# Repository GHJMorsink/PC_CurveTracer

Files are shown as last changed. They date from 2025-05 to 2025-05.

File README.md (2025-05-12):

# PC_CurveTracer

*Curve tracing for bjt transistors, FETs, diodes and more through ATMega micro and PC*

## Introduction

This project builds an I-V Curve Tracer connected to a computer using USB. A curve tracer is a type of instrument used to 
measure the current through a device with varying voltages across it. It is a specialized piece of electronic test equipment 
to analyze the characteristics of discrete electronic components, such as diodes, and transistors. The device contains 
voltage and current sources that can be used to stimulate the device under test (DUT). The curve tracer applies a continuously 
varying voltage to two terminals of the device under test and measure the amount of current that the device permits to flow 
at each voltage. This so-called I-V (current versus voltage) data is directly displayed on an oscilloscope screen in X-Y mode.
Examples of full featured Curve tracers which can go to more than 100 Volt and currents into several amps are the Textronix 576, 577, 
and the Leader LTC-905. Simpler (and cheaper) solutions are based on a simple transformer with a few resistors like 
in [Changpuak's curvetracer](https://www.changpuak.ch/electronics/Curve_Tracer_advanced.php). All of these need an oscilloscope 
as the display device.
This project builds one which does not use an oscilloscope, but shows the data, and the controls on a computer. The interface 
to the computer is through USB, and the power is also taken from the USB connection. This means the device can only handle 
signal-sized discrete components up to 5 Volt and a maximum of about 10 mAmpere.

## Hardware

The hardware used is based on a simple microcontroller (good old Atmel ATMega8) which generates the varying voltages with two PWM-DAC based outputs. 
The measurements are done with the internal ADC. For switching between NPN and PNP transistors (or N-mosfets and P-mosfets) one 
of the digital outputs is used.
The USB connection is based on the V-USB package of OBDev [V-USB](https://github.com/obdev/v-usb).
The power section for the DUT contains an opamp for buffering the DAC output, so it can sink and source currents. The resistor 
measures the current and creates at the same time a current limiting function. The second opamp is arranged as a current to 
voltage convertor with some gain so that about 10 mA gives a full scale for the ADC. Note that the ground reference for the 
floating current convertor is switched to accommodate for positive and negative currents. Also be aware the opamp’s inputs 
and outputs must reach rail to rail voltages. The control connection for the DUT (the base, or the gate) has fairly simple set-up 
from the second PWM-DAC with one RC-filter and a high value resistor; FETs get a voltage, bipolar transistors get a small current.

## Firmware

To be able to connect to the device without needing a software driver, the system will work as a HID device. Communication will 
be on the features report channel. The device and the used protocol has the capacity for 16 different modes with each 8 functions. 
At the moment only the mode for measuring a trace and resetting (for firmware updates) are implemented. The functions are 
initializing, reading measurements, and reading and setting calibration data. More modes and funtions can be created in the 
future; there is still enough room on an ATMega8. One can think of an automated hFE measurement mode and likewise modes for FETs.
Creating one trace is done by the initializing command containing the info for the used bias voltage (and this determines 
directly the bias current in cases of bipolar transistors), the number of measurement points, and the polarity to be used. 
After the initialization the requested number of measurements can be retrieved. There are also commands for setting and reading 
calibration values, which are needed for correction of the current to voltage conversion. The calibration is used at PC 
software level, and stored on the device because it is 'attached' to the components of that device.

The firmware contains a hid-based usb bootloader. This helps in a simple system where updates of the firmware can be transported 
conveniently to the device. The software supports this mechanism (it was used heavily during development).

## Software

The controlling GUI is built using a Python script. The graphics are made using the PyQT and pyqtgraph packages. The connection 
with the device is through USB using the pywinusb package. Starting the GUI through main.py gives the following window:
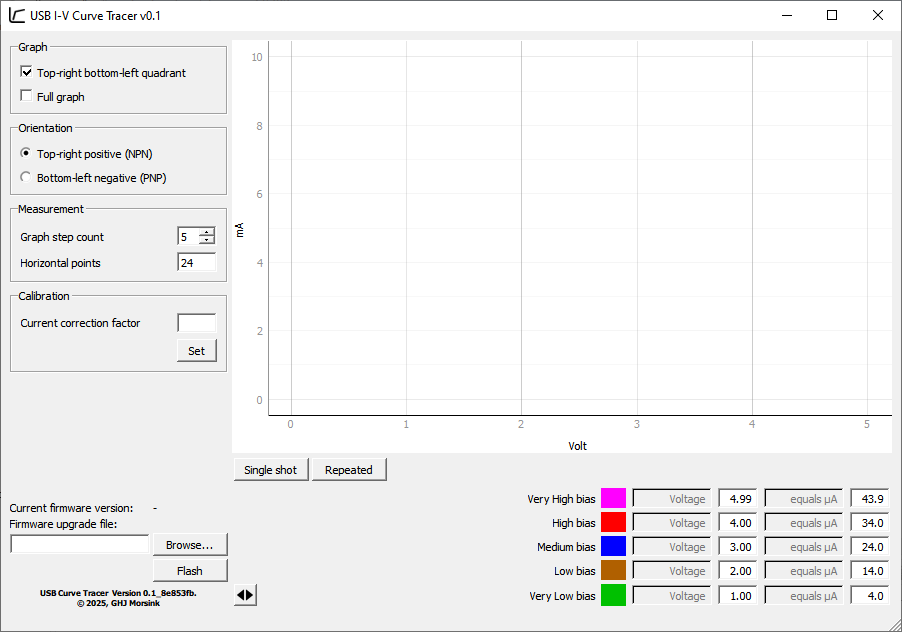
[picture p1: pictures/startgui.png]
startup image


It defaults to top-right quadrant for 5 traces, good for a normal npn transistor.

Within the application it is possible to update the firmware, so new features can be introduced. There is also a bootload.py 
script which gives the possibility to update the firmware or give it the initial firmware using the console.

## Results and calibration

Connecting the hardware to the computer, and starting the software conveniently through the CurveTracer.bat file gives the 
opportunity to calibrate it. This calibration is necessary only once. Put a 1kOhm resistor (1%) in the hardware between the collector 
and emitter pins, and do a 'single shot' measurement. You should see a straight line through points 0mA/0V,  1mA/1V,  2mA/2V, and 3mA/3V. 
If the line isn't correct, you can adjust it by changing the 'Current correction voltage', 'Set' it, and do a new measurement.
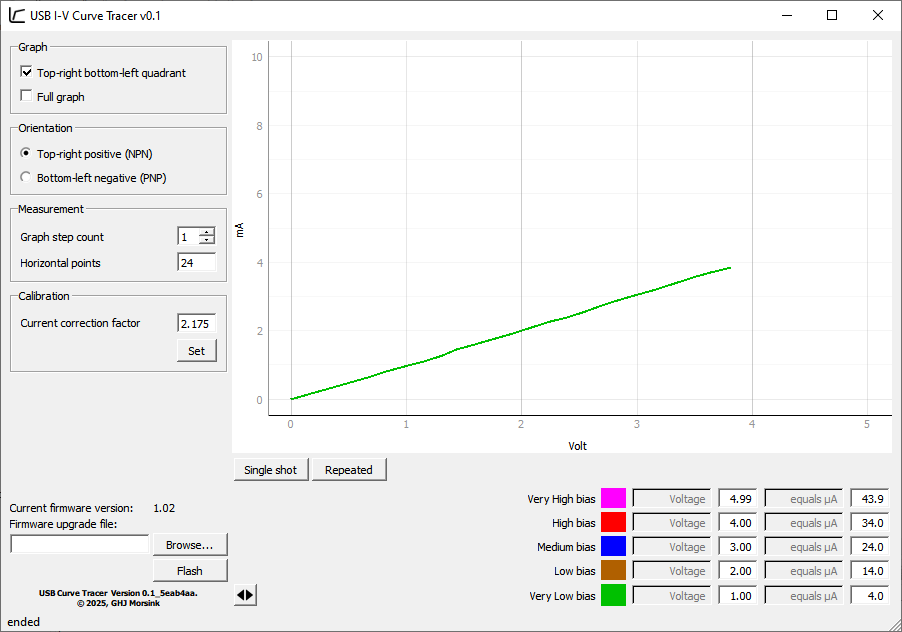
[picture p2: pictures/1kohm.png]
1kOhm image


A view of some other measurements are in the next pictures. A LED, a pnp transistor (BC213) and a npn transistor (2SC945). The last 
one in full graph mode: you get a single trace in the opposite quadrant, without any base/gate stimulation.
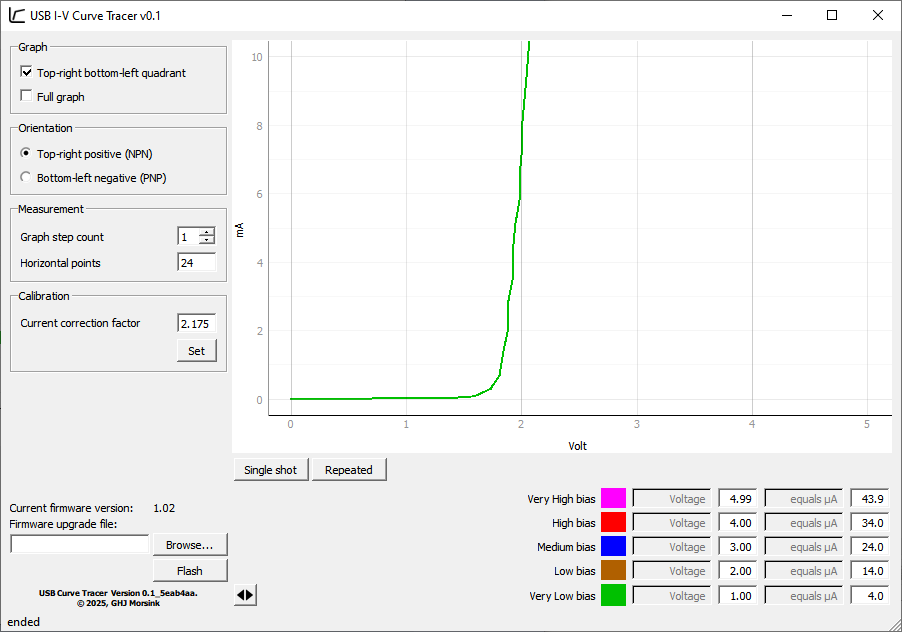
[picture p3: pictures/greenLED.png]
Green LED image

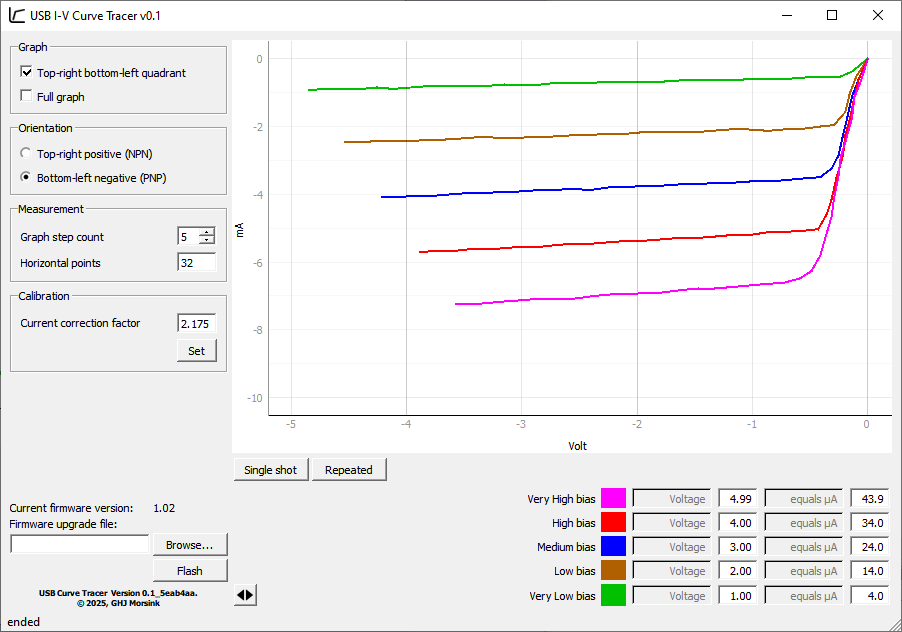
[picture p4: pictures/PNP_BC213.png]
BC213 PNP image

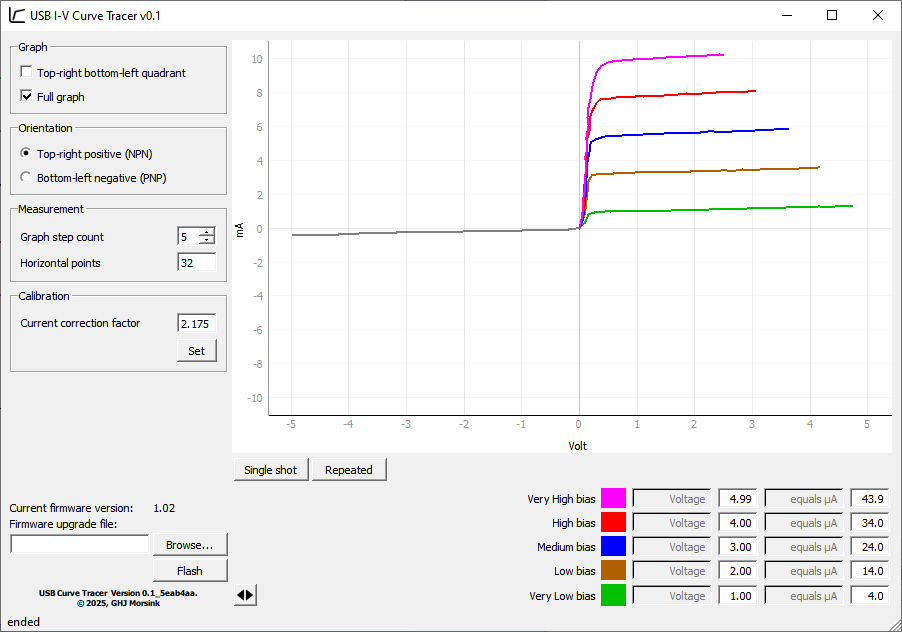
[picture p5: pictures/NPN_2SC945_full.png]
Full NPN 2SC945 image


Note: You can right-click on the graph for saving the picture and other goodies, supplied out of the box from the pyqtgraph package.

## Tooling and other notes

The hardware is developed with a somewhat older version of CadSoft's EAGLE pcb design software, now part of Autodesk Fusion Software.
Version 7.5.0 was used. For reference the schematic and the pcb design are also given as pdf document.
The firmware is written using the Microchip Studio 7.0 environment. You can get it through the URL [https://www.microchip.com/en-us/tools-resources](https://www.microchip.com/en-us/tools-resources/develop/microchip-studio#Downloads); older Atmel versions will work as well. 
The firmware is with minor or no changes also usable on the ATMega88 and the bigger ATMega168 and ATMega328. The fuse settings 
for the microcontroller can be found in the document [Fuses.txt](./embedded/fuses.txt).
For convenience a hex file containing the image for the application and the bootloader is in the file ./embedded/full.hex.
The PC software is fully based o Python. Version 3.12 was used during development, any version in the 3-series should be fine. 
The requirements.txt contains the names of the needed packages to conveniently install them using 'pip'. For users who want to 
adapt/develop the software to their likings, it is advised to install QT Designer as well.

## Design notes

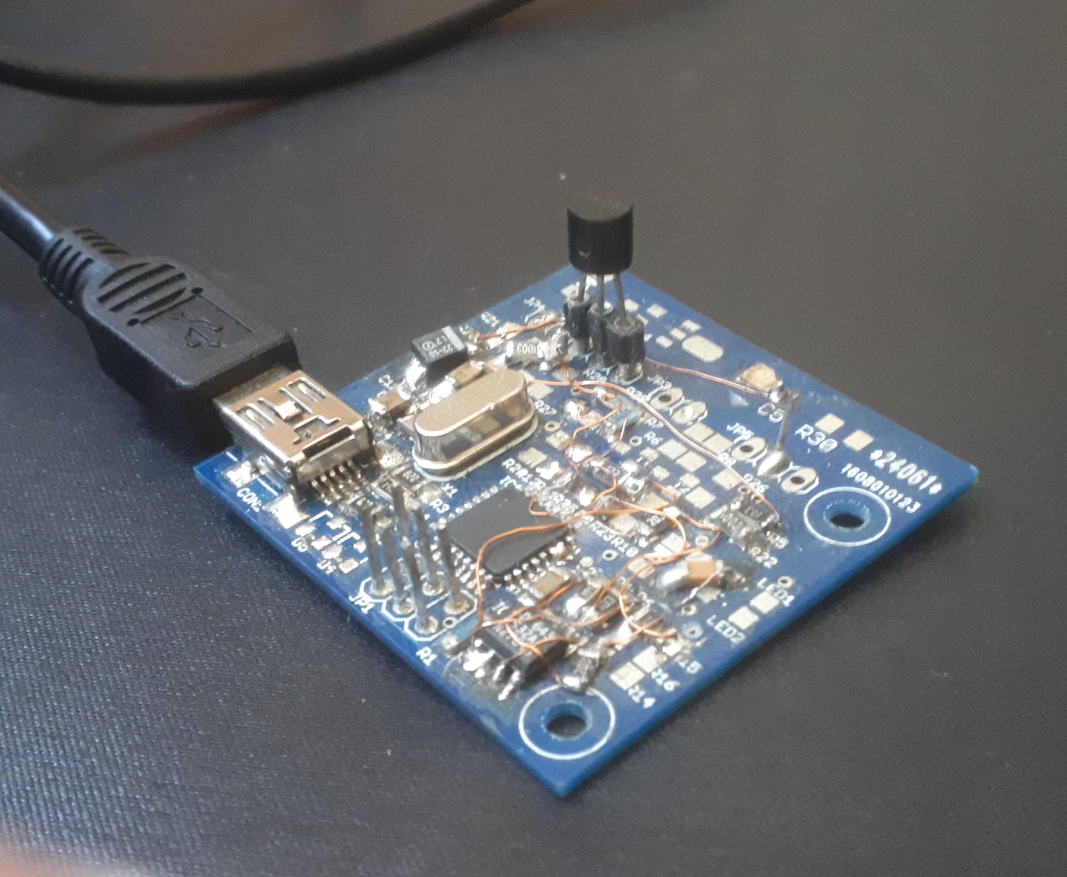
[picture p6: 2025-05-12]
pictures/prototype.jpg

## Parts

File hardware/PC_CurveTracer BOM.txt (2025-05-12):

Partlist exported from D:/projects/PC_CurveTracer/hardware/PC_CurveTracer.sch at 06/05/2025 17:49

Part Value     Device                       Package   Description                                MF MPN          NP OC_FARNELL OC_NEWARK VOLTAGE
C1   100n      C-EUC1206                    C1206     CAPACITOR, European symbol                                                                
C2   100n      C-EUC1206                    C1206     CAPACITOR, European symbol                                                                
C3   22p       C-EUC0603                    C0603     CAPACITOR, European symbol                                                                
C4   22p       C-EUC0603                    C0603     CAPACITOR, European symbol                                                                
C5   22n       C-EUC1206                    C1206     CAPACITOR, European symbol                                                                
C6   100n      C-EUC1206                    C1206     CAPACITOR, European symbol                                                                
C7   220p      C-EUC1206                    C1206     CAPACITOR, European symbol                                                                
C10  10uF      CPOL-EUSMCC                  SMC_C     POLARIZED CAPACITOR, European symbol                                               16V    
CON1 MINI-USB  MINI-USB_SHIELD5P4-32005-400 32005-400 MINI USB-B R/A W/O POST 5 pol.                                unknown    unknown          
D1   DUT       ZENER-DIODESOD80C            SOD80C    Z-Diode                                                                                   
D2   GREEN     LEDSML0805                   SML0805   LED                                                                                       
D3   BZX84C3V6 BZX84CSMD                    TO236     Z DIODE                                                    NP                             
D4   BZX84C3V6 BZX84CSMD                    TO236     Z DIODE                                                    NP                             
IC1  MEGA8-AI  MEGA8-AI                     TQFP32-08 MICROCONTROLLER                               ATMEGA8-16AU    9171371    73M8863          
IC2  TLC272B   LM358D                       SO08      OP AMP also LM158; LM258; LM2904                                                          
JP1  ISP       PINHD-2X3                    2X03      PIN HEADER                                                                                
JP2  SERIAL    PINHD-1X6                    1X06      PIN HEADER                                                                                
JP3  DEVICE    PINHD-1X5                    1X05      PIN HEADER                                                                                
L1   Ferrite   BLM15HG601SN1                0402      EMIFIL (R) Chip Ferrite Bead for GHz Noise                                                
R1   10K       R-EU_R1206                   R1206     RESISTOR, European symbol                                                                 
R2   82        R-EU_R1206                   R1206     RESISTOR, European symbol                                                                 
R3   82        R-EU_R1206                   R1206     RESISTOR, European symbol                                                                 
R4   1K8       R-EU_R1206                   R1206     RESISTOR, European symbol                                                                 
R5   470       R-EU_R1206                   R1206     RESISTOR, European symbol                                                                 
R6   220       R-EU_R1206                   R1206     RESISTOR, European symbol                                                                 
R7   10K       R-EU_R1206                   R1206     RESISTOR, European symbol                                                                 
R8   100K      R-EU_R1206                   R1206     RESISTOR, European symbol                                                                 
R9   47        R-EU_R1206                   R1206     RESISTOR, European symbol                                                                 
R10  100       R-EU_R1206                   R1206     RESISTOR, European symbol                                                                 
R11  20K       R-EU_R1206                   R1206     RESISTOR, European symbol                                                                 
R12  10K       R-EU_R1206                   R1206     RESISTOR, European symbol                                                                 
R13  20K       R-EU_R1206                   R1206     RESISTOR, European symbol                                                                 
R14  10K       R-EU_R1206                   R1206     RESISTOR, European symbol                                                                 
R15  10K       R-EU_R1206                   R1206     RESISTOR, European symbol                                                                 
T1   TUT       BC846                        SOT23     NPN TRANSISTOR                                                                            
T2   TUT       -PNP-SOT89-ECB               SOT89-ECB PNP Transistror                                                                           
X1   12MHz     CRYSTALHC49S                 HC49/S    CRYSTAL                                                       1667008    unknown

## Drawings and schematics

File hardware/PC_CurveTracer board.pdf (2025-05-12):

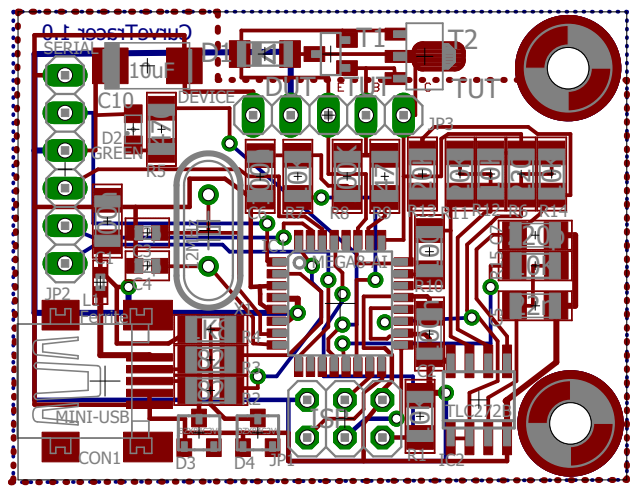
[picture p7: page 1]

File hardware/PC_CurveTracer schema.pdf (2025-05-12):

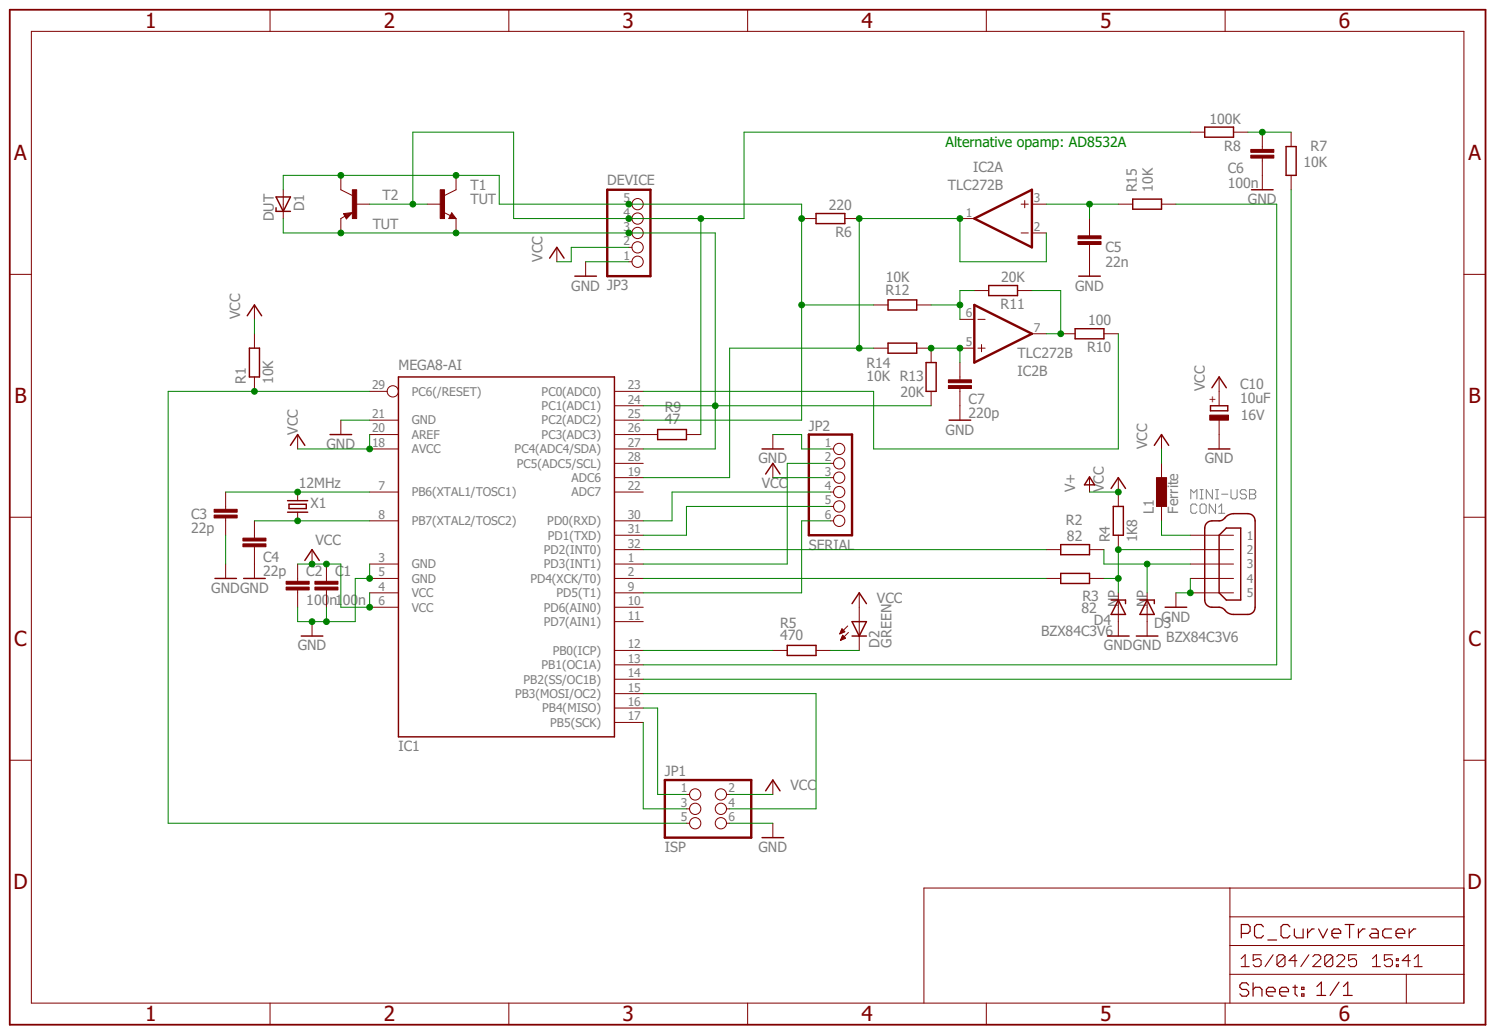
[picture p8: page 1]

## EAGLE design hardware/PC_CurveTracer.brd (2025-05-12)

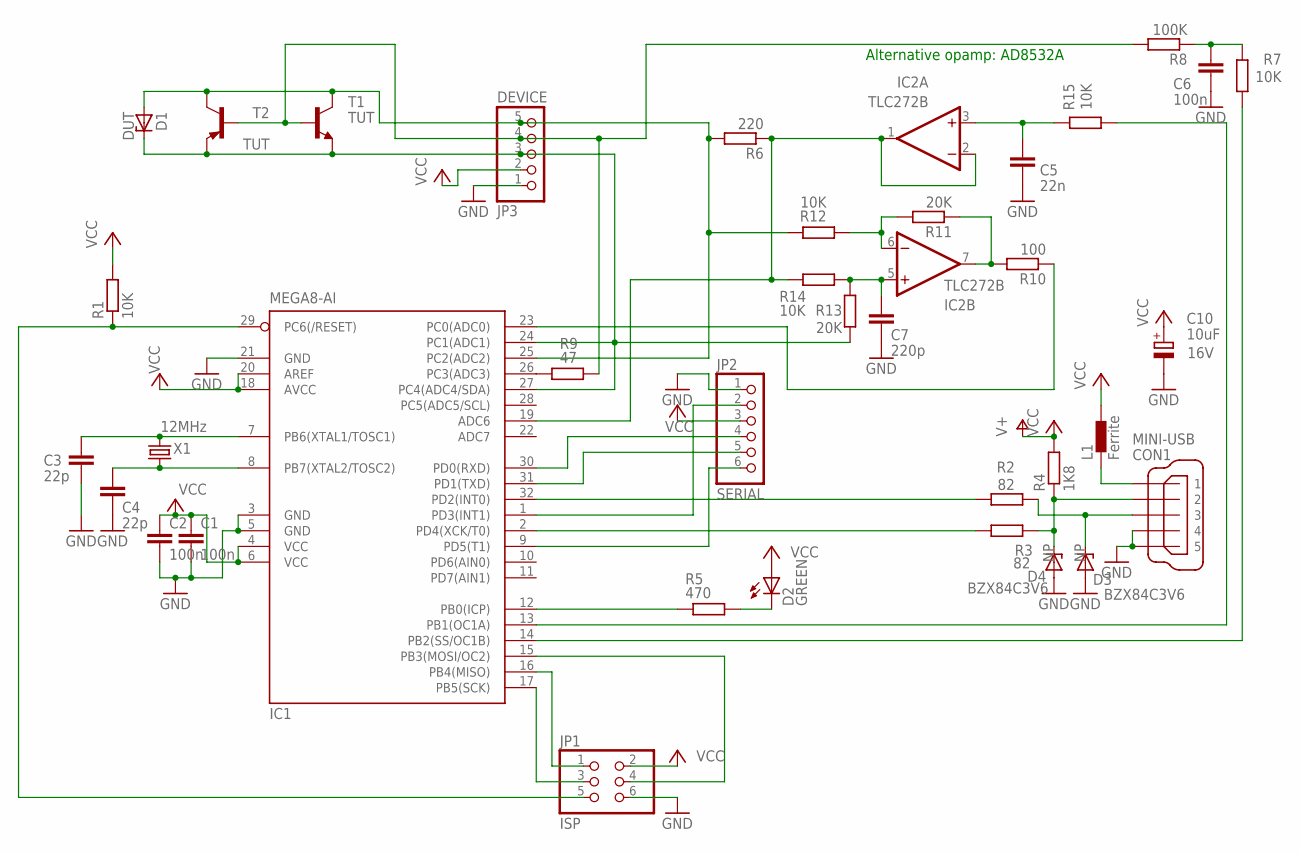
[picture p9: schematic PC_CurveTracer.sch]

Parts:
C1, C2, C6: 100n; C1206
C3, C4: 22p; C0603
C5: 22n; C1206
C7: 220p; C1206
C10: 10uF; SMC_C; VOLTAGE 16V
CON1: MINI-USB; 32005-400
D1: DUT; SOD80C
D2: GREEN; SML0805
D3, D4: BZX84C3V6; TO236
IC1: MEGA8-AI; TQFP32-08
IC2: TLC272B; SO08
JP1: ISP; 2X03
JP2: SERIAL; 1X06
JP3: DEVICE; 1X05
L1: Ferrite; 0402
R1, R7, R12, R14, R15: 10K; R1206
R2, R3: 82; R1206
R4: 1K8; R1206
R5: 470; R1206
R6: 220; R1206
R8: 100K; R1206
R9: 47; R1206
R10: 100; R1206
R11, R13: 20K; R1206
T1: TUT; SOT23
T2: TUT; SOT89-ECB
X1: 12MHz; HC49/S

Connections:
GND: C1.2, C2.2, C3.2, C4.2, C5.2, C6.2, C7.2, C10.-, CON1.4, CON1.5, D3.A, D4.A, IC1.3 (GND), IC1.5 (GND), IC1.21 (GND), IC2.4 (GND), JP1.6, JP2.1, JP3.1
unnamed: IC1.29 (PC6(/RESET)), JP1.5, R1.1
unnamed: D2.C, R5.1
unnamed: C3.1, IC1.7 (PB6(XTAL1/TOSC1)), X1.2
unnamed: C4.1, IC1.8 (PB7(XTAL2/TOSC2)), X1.1
unnamed: IC1.16 (PB4(MISO)), JP1.1
unnamed: CON1.1, L1.1
unnamed: IC1.15 (PB3(MOSI/OC2)), JP1.4
unnamed: IC1.12 (PB0(ICP)), R5.2
unnamed: IC1.32 (PD2(INT0)), R2.2
unnamed: IC1.1 (PD3(INT1)), JP2.2
unnamed: CON1.3, D3.C, R2.1
unnamed: IC1.30 (PD0(RXD)), JP2.4
unnamed: IC1.2 (PD4(XCK/T0)), R3.2
unnamed: CON1.2, D4.C, R3.1, R4.1
unnamed: IC1.13 (PB1(OC1A)), R15.1
unnamed: C6.1, R7.2, R8.1
unnamed: IC2.6 (-IN), R11.2, R12.1
unnamed: IC1.31 (PD1(TXD)), JP2.5
unnamed: D1.C, IC1.24 (PC1(ADC1)), IC1.27 (PC4(ADC4/SDA)), JP3.3, R13.1, T1.2 (E), T2.E
unnamed: IC1.9 (PD5(T1)), JP2.6
unnamed: IC1.23 (PC0(ADC0)), R10.1
unnamed: IC1.26 (PC3(ADC3)), R9.1
unnamed: IC1.19 (ADC6), IC2.1 (OUT), IC2.2 (-IN), R6.1, R14.2
unnamed: IC2.7 (OUT), R10.2, R11.1
unnamed: IC1.14 (PB2(SS/OC1B)), R7.1
unnamed: D1.A, IC1.25 (PC2(ADC2)), JP3.5, R6.2, R12.2, T1.3 (C), T2.C
unnamed: C7.1, IC2.5 (+IN), R13.2, R14.1
unnamed: IC1.17 (PB5(SCK)), JP1.3
unnamed: C5.1, IC2.3 (+IN), R15.2
TUT: JP3.4, R8.2, R9.2, T1.1 (B), T2.B
VCC: C1.1, C2.1, C10.+, D2.A, IC1.4 (VCC), IC1.6 (VCC), IC1.18 (AVCC), IC1.20 (AREF), IC2.8 (VCC), JP1.2, JP2.3, JP3.2, L1.2, R1.2, R4.2

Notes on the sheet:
Alternative opamp: AD8532A

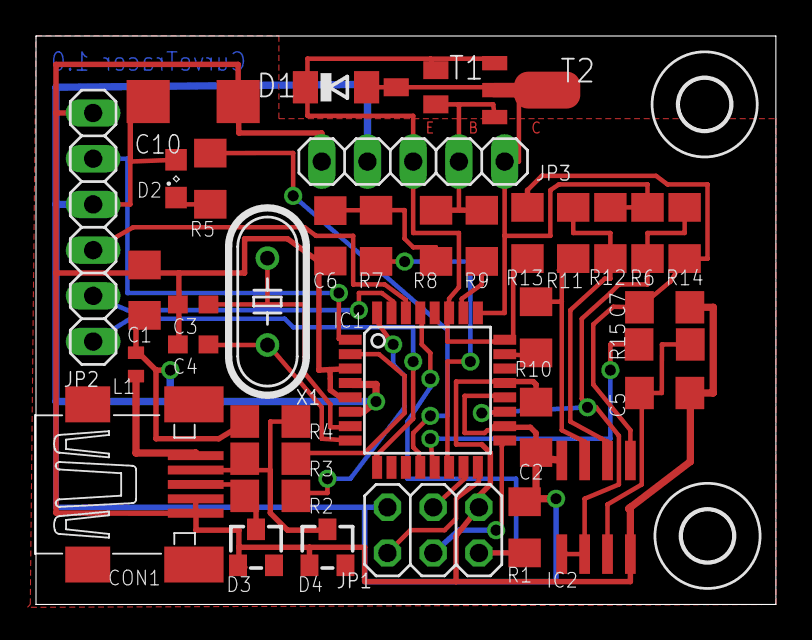
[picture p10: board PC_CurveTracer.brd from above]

Board: 2 copper layers, 41.1 x 31.6 mm, 39 parts (0 on the bottom side), 32 nets.

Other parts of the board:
HOLE1, HOLE2: -; 2,8

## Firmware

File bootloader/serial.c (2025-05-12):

/*----------------------------------------------------------------------------

 Copyright 2011, GHJ Morsink


 Author: MorsinkG

   Purpose:
      Implements serial function

   Contains:

   Module:
      main

------------------------------------------------------------------------------
*/
/***------------------------- Includes ----------------------------------***/
#include "defines.h"

#if TEST_MODE

#include <avr/io.h>
#include <avr/interrupt.h>
#include <avr/pgmspace.h>
#include "serial.h"

/***------------------------- Defines -----------------------------------***/

/* The serial buffer takes xx bytes + 2 pointers */
#define SERIAL_RXBUFFERSIZE      40     /* receive buffer size (keep below 256)*/
#define SERIAL_TXBUFFERSIZE      255    /* transmit buffer size (keep below 256)*/
#define MAIN_CLK                 12000000      /* System runs at 12 MHz */

#if defined(__AVR_ATmega8__)
#define AT8		1
#else
#define	AT8		0
#endif

/***----------------------- Local Types ---------------------------------***/

/***------------------------- Local Data --------------------------------***/
/* The data is given as flat types; structures give overhead in the generated code */
static uint8_t    acRxBuffer[ SERIAL_RXBUFFERSIZE ];
static uint8_t    iRxInPtr;
static uint8_t    iRxOutPtr;

static uint8_t    acTxBuffer[ SERIAL_TXBUFFERSIZE ];
static uint8_t    iTxInPtr;
static uint8_t    iTxOutPtr;

static uint16_t   const uBaudDetails[7] PROGMEM =
{
   (((MAIN_CLK / 2400) / 8) - 1),
   (((MAIN_CLK / 4800) / 8) - 1),
   (((MAIN_CLK / 9600) / 8) - 1),
   (((MAIN_CLK / 19200) / 8) - 1),
   (((MAIN_CLK / 38400) / 8) - 1),
   (((MAIN_CLK / 57600) / 8) - 1),
   (((MAIN_CLK / 115200L) / 8) - 1)
};

/***------------------------ Global Data --------------------------------***/

uint8_t uRxOverflow;
uint8_t uTxOverflow;

/***------------------------ Local functions ----------------------------***/

/***------------------------ Global functions ---------------------------***/
#if AT8
/*--------------------------------------------------
Baudrate setting
 --------------------------------------------------*/
void vSetBaud( uint8_t uBaudrate )
{
   uint16_t uBaudReg;

   uBaudReg = pgm_read_word( &uBaudDetails[ uBaudrate - 1 ] );
   UBRRH = ( (uBaudReg) >> 8) & 0x0f;
   UBRRL =   (uBaudReg)       & 0xff;
}
#else
/*--------------------------------------------------
Baudrate setting
 --------------------------------------------------*/
void vSetBaud( uint8_t uBaudrate )
{
   uint16_t uBaudReg;

   uBaudReg = pgm_read_word( &uBaudDetails[ uBaudrate - 1 ] );
   UBRR0H = ( (uBaudReg) >> 8) & 0x0f;
   UBRR0L =   (uBaudReg)       & 0xff;
}
#endif

/*--------------------------------------------------
 Initialize UART
 --------------------------------------------------*/
#if AT8
void vSerialInit( void )
{
   UCSRA = 2;
   UCSRB = _BV(RXEN) | _BV(RXCIE) | _BV(TXEN);
   UCSRC = _BV(URSEL) | _BV(UCSZ0) | _BV(UCSZ1);

   iRxInPtr = 0;                        /* purge all buffers */
   iRxOutPtr = 0;
   iTxInPtr = 0;
   iTxOutPtr = 0;
   vSetBaud( 5 );          /* set a default baudrate (overwritten by the user) */
   uTxOverflow = 0;
   uRxOverflow = 0;
}
#else
void vSerialInit( void )
{
	UCSR0A = 2;
	UCSR0B = _BV(RXEN0) | _BV(RXCIE0) | _BV(TXEN0);
	UCSR0C = _BV(UCSZ00) | _BV(UCSZ01);

	iRxInPtr = 0;                        /* purge all buffers */
	iRxOutPtr = 0;
	iTxInPtr = 0;
	iTxOutPtr = 0;
	vSetBaud( 3 );          /* set a default baudrate (overwritten by the user) */
	uTxOverflow = 0;
	uRxOverflow = 0;
}
#endif
/*--------------------------------------------------
 Get characters non-blocking from the receiver
 --------------------------------------------------*/
uint8_t uSerialGetChar( uint8_t *uRcv )
{
    if ( iRxInPtr != iRxOutPtr )  /* check if something in buffer */
    {
        *uRcv = acRxBuffer[ iRxOutPtr ];
        iRxOutPtr += 1;
        if ( iRxOutPtr == SERIAL_RXBUFFERSIZE )
        {
            iRxOutPtr = 0;
        }
        return RESULT_SUCCESS;                 /* report success */
    }
    return RESULT_ERROR;
}

/*--------------------------------------------------
 Check size of open locations in transmit buffer
 --------------------------------------------------*/
uint8_t uSerialGetFree( void )
{
   if ( iTxInPtr >= iTxOutPtr )
   {
      return (SERIAL_TXBUFFERSIZE - (iTxInPtr - iTxOutPtr));
   }
   return (iTxOutPtr - iTxInPtr);
}


/* Put a character to transmit */
#if AT8
/*--------------------------------------------------
Put a character to transmit; if no room: silently ignore
 --------------------------------------------------*/
void vSerialPutChar(uint8_t uTx)
{
   uint8_t     uNextPtr;

   uNextPtr = iTxInPtr + 1;
   if ( uNextPtr >= SERIAL_TXBUFFERSIZE )
   {
      uNextPtr = 0;
   }
   if ( iTxOutPtr != uNextPtr )         /*  check there is room  */
   {
      acTxBuffer[ iTxInPtr ] = uTx;
      /* Now the next items must be without an tx-out interrupt */
      cli();
      iTxInPtr = uNextPtr;
      UCSRB = _BV(RXEN)|_BV(RXCIE)|_BV(TXEN)|_BV(UDRIE); /* interrupt was off: set it on */
      sei();
   }
   else
   {
      uTxOverflow += 1;                 /* overflow situation */
   }
}

/*--------------------------------------------------
 Receiving interrupt
 --------------------------------------------------*/
ISR(USART_RXC_vect)
{
   uint8_t uNextPtr;

   uNextPtr = iRxInPtr + 1;
   if ( uNextPtr >= SERIAL_RXBUFFERSIZE )
   {
      uNextPtr = 0;
   }
   if ( iRxOutPtr != uNextPtr )         /*  check there is room  */
   {
      acRxBuffer[ iRxInPtr ] = UDR;
      iRxInPtr = uNextPtr;
   }
   else
   {
      uRxOverflow += 1;
   }
}

/*--------------------------------------------------
 Transmitting interrupt
 --------------------------------------------------*/
ISR( USART_UDRE_vect )
{
   if ( iTxInPtr != iTxOutPtr )  /* check if something in buffer */
   {
      UDR = acTxBuffer[ iTxOutPtr ];
      iTxOutPtr += 1;
      if ( iTxOutPtr >= SERIAL_TXBUFFERSIZE )
      {
         iTxOutPtr = 0;
      }
   }
   if ( iTxOutPtr == iTxInPtr )        /* if nothing in the buffer (anymore) */
   {
      UCSRB = _BV(RXEN)|_BV(RXCIE)|_BV(TXEN);  /* switch off the interrupt */
   }
}

#else
/*--------------------------------------------------
Put a character to transmit; if no room: silently ignore
 --------------------------------------------------*/
void vSerialPutChar(uint8_t uTx)
{
   uint8_t     uNextPtr;

   uNextPtr = iTxInPtr + 1;
   if ( uNextPtr >= SERIAL_TXBUFFERSIZE )
   {
      uNextPtr = 0;
   }
   if ( iTxOutPtr != uNextPtr )         /*  check there is room  */
   {
      acTxBuffer[ iTxInPtr ] = uTx;
      /* Now the next items must be without an tx-out interrupt */
      cli();
      iTxInPtr = uNextPtr;
      UCSR0B = _BV(RXEN0)|_BV(RXCIE0)|_BV(TXEN0)|_BV(UDRIE0); /* interrupt was off: set it on */
      sei();
   }
   else
   {
      uTxOverflow += 1;                 /* overflow situation */
   }
}

/*--------------------------------------------------
 Receiving interrupt
 --------------------------------------------------*/
ISR(USART_RX_vect)
{
   uint8_t uNextPtr;

   uNextPtr = iRxInPtr + 1;
   if ( uNextPtr >= SERIAL_RXBUFFERSIZE )
   {
      uNextPtr = 0;
   }
   if ( iRxOutPtr != uNextPtr )         /*  check there is room  */
   {
      acRxBuffer[ iRxInPtr ] = UDR0;
      iRxInPtr = uNextPtr;
   }
   else
   {
      uRxOverflow += 1;
   }
}

/*--------------------------------------------------
 Transmitting interrupt
 --------------------------------------------------*/
ISR( USART_UDRE_vect )
{
   if ( iTxInPtr != iTxOutPtr )  /* check if something in buffer */
   {
      UDR0 = acTxBuffer[ iTxOutPtr ];
      iTxOutPtr += 1;
      if ( iTxOutPtr >= SERIAL_TXBUFFERSIZE )
      {
         iTxOutPtr = 0;
      }
   }
   if ( iTxOutPtr == iTxInPtr )        /* if nothing in the buffer (anymore) */
   {
      UCSR0B = _BV(RXEN0)|_BV(RXCIE0)|_BV(TXEN0);  /* switch off the interrupt */
   }
}
#endif

#endif                                  /* TEST_MODE */
/* EOF */
